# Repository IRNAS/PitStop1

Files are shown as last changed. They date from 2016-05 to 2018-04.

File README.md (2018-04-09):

# PitStop1 - Open source turtle tag and turtle camera enclosure
PitStop1 is open source turtle tag enclosure we developed in collaboration with the [Arribada Initiative](http://blog.arribada.org/). Turtle tags are used to track the movement of turtles and collect the information necessary to design better strategies for their conservation.

In this repository you can find all technical documentation for the latest version of the turtle tag enclosure and the turtle camera enclosure. The documentation for the version 1 of Pitstop1 is available in the branch [version-1](https://github.com/IRNAS/PitStop1/tree/version1).

Read [an article about the open source turtle tags and the development process](https://www.wildlabs.net/resources/case-studies/how-open-source-technologies-could-dramatically-reduce-cost-tagging-green-sea) and get in touch with [us at Institute IRNAS](http://irnas.eu) for customization and orders.

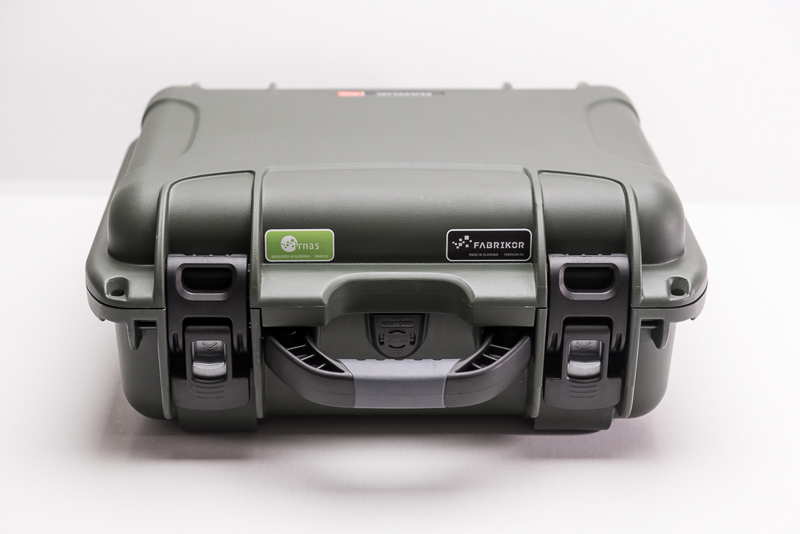
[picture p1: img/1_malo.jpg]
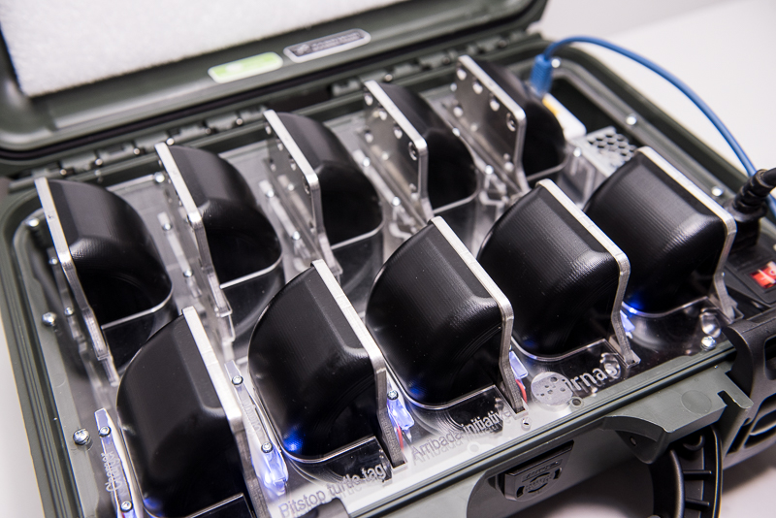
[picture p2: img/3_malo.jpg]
    

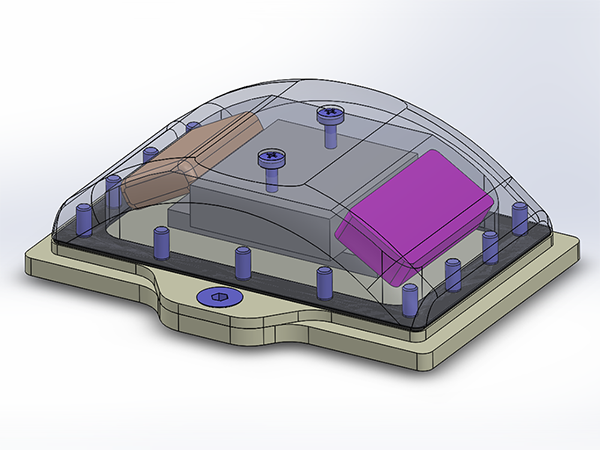
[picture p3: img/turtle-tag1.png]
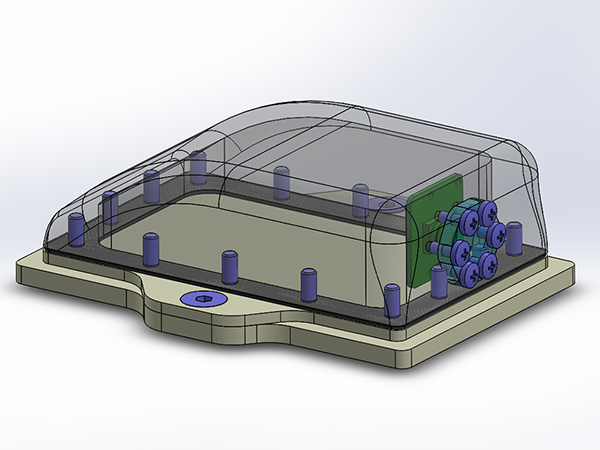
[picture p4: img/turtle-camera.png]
 

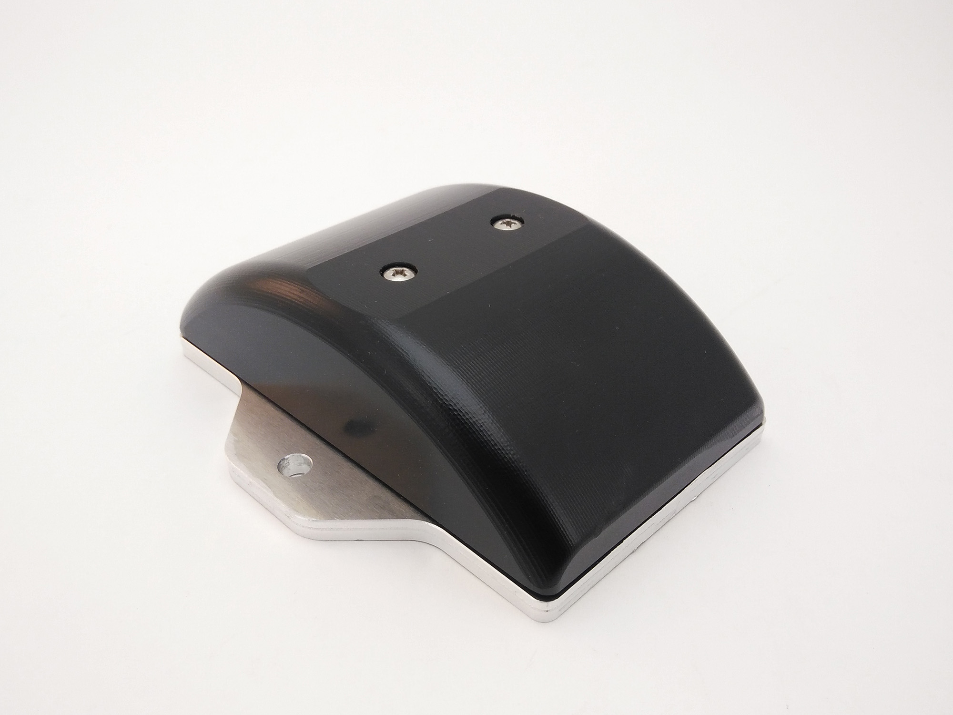
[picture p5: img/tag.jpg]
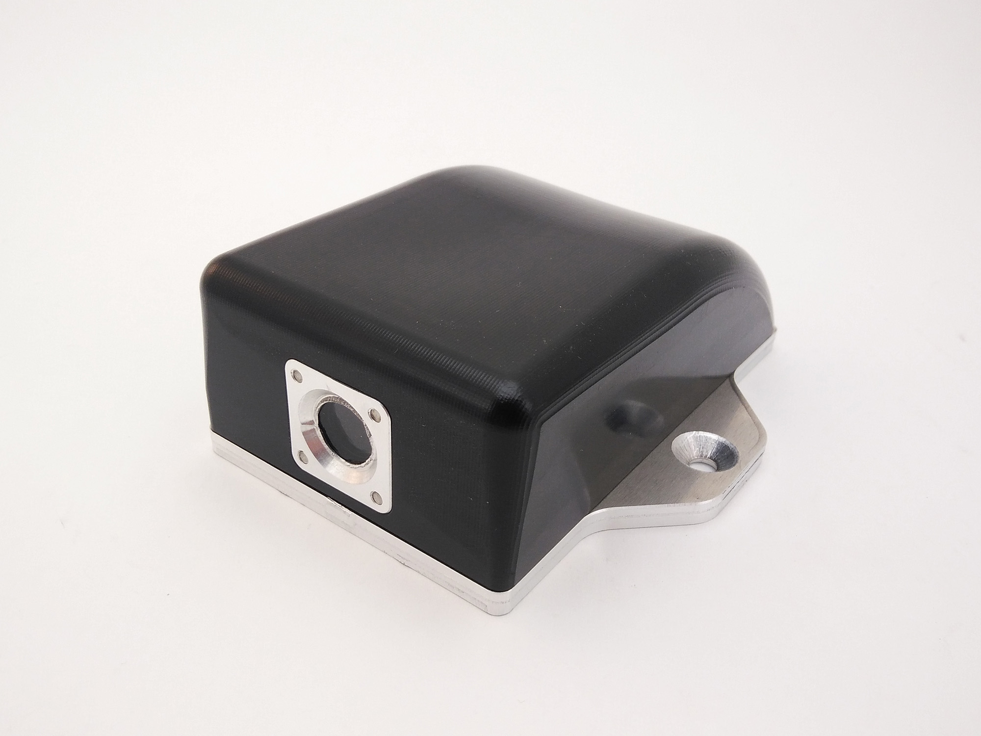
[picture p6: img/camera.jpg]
 

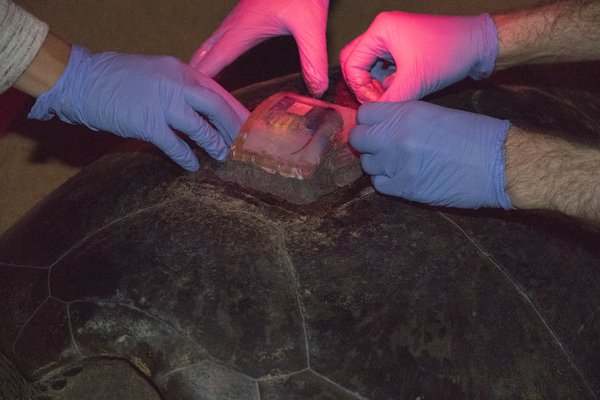
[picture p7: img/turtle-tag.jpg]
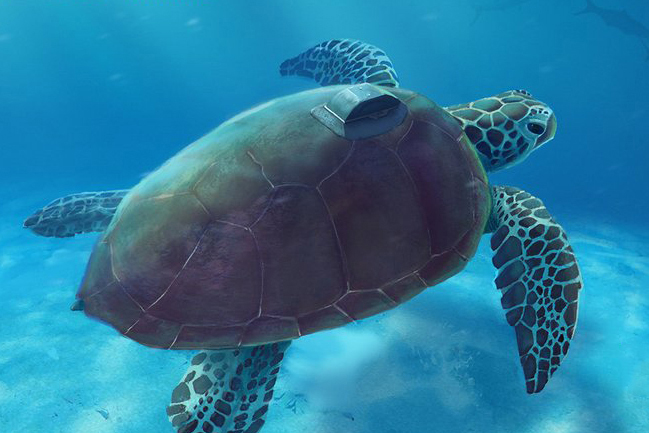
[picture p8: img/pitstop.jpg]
 
*Copyright: The Arribada Initiative*

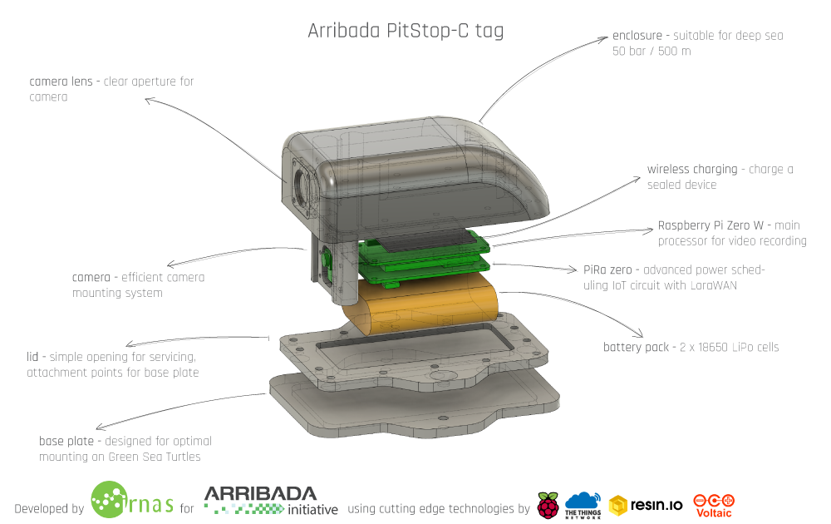
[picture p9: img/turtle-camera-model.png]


#### Testing

The enclosure has to sustain in extreme circumstances while mounted on the turtle, such as being hit by rocks, the turtle rubs its shell at, or high pressure at depths up to 200m. To determine what material and sealing to use for the enclosure we did a series of <a href="https://github.com/IRNAS/PitStop1/tree/master/testing">tests</a>.

---

#### License

All our projects are as usefully open-source as possible.

Hardware including documentation is licensed under [CERN OHL v.1.2. license](http://www.ohwr.org/licenses/cern-ohl/v1.2)

Firmware and software originating from the project is licensed under [GNU GENERAL PUBLIC LICENSE v3](http://www.gnu.org/licenses/gpl-3.0.en.html).

Open data generated by our projects is licensed under [CC0](https://creativecommons.org/publicdomain/zero/1.0/legalcode).

All our websites and additional documentation are licensed under [Creative Commons Attribution-ShareAlike 4 .0 Unported License] (https://creativecommons.org/licenses/by-sa/4.0/legalcode).

What this means is that you can use hardware, firmware, software and documentation without paying a royalty and knowing that you'll be able to use your version forever. You are also free to make changes but if you share these changes then you have to do so on the same conditions that you enjoy.

Koruza, GoodEnoughCNC and IRNAS are all names and marks of Institut IRNAS Rače.
You may use these names and terms only to attribute the appropriate entity as required by the Open Licences referred to above. You may not use them in any other way and in particular you may not use them to imply endorsement or authorization of any hardware that you design, make or sell.

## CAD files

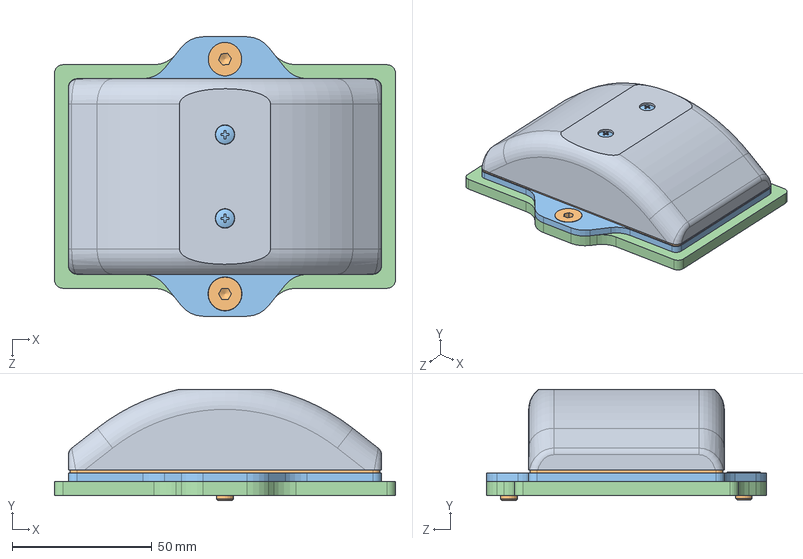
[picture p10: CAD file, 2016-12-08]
source/turtle tag.SLDASM
122.0 x 39.9 x 100.0 mm
case
gasket
lid
base plate
meraki
AX3
i-gotU
battery 1050mAh LiPo
screw_HEX_SOCKET_DIN7991_M4x12_8.8 x 14
screw_HEX_SOCKET_DIN7991_M6x10_8.8 x 2
screw_selfsealing_phillips_335-1156-ND_M3x8 x 2

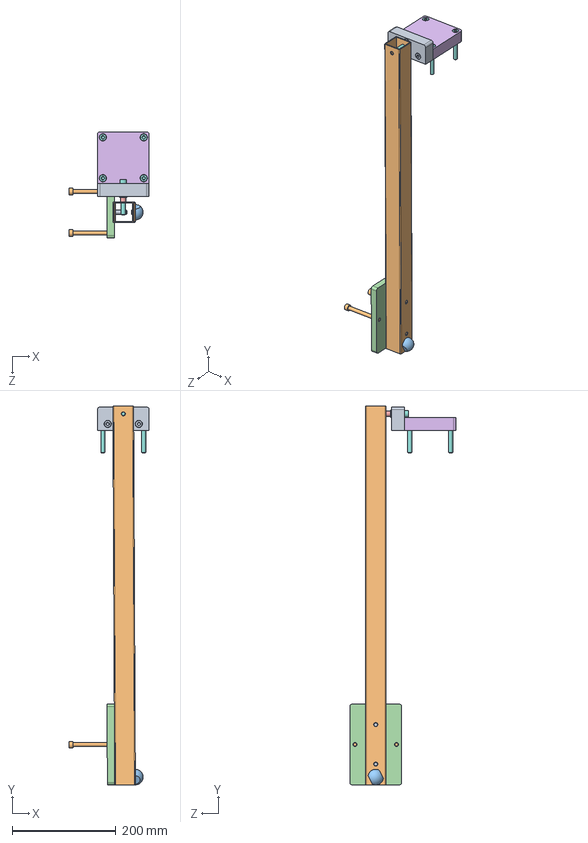
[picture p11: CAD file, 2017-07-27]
testing/durability/pendulum/Assembly.SLDASM
155.0 x 730.2 x 205.0 mm
holder2
lever
backplate
spacer
holder1
DIN 912 M5 x 12
DIN 912 M8 x 60 x 5
DIN 912 M8 x 30 x 4
DIN 912 M8 x 80 x 2

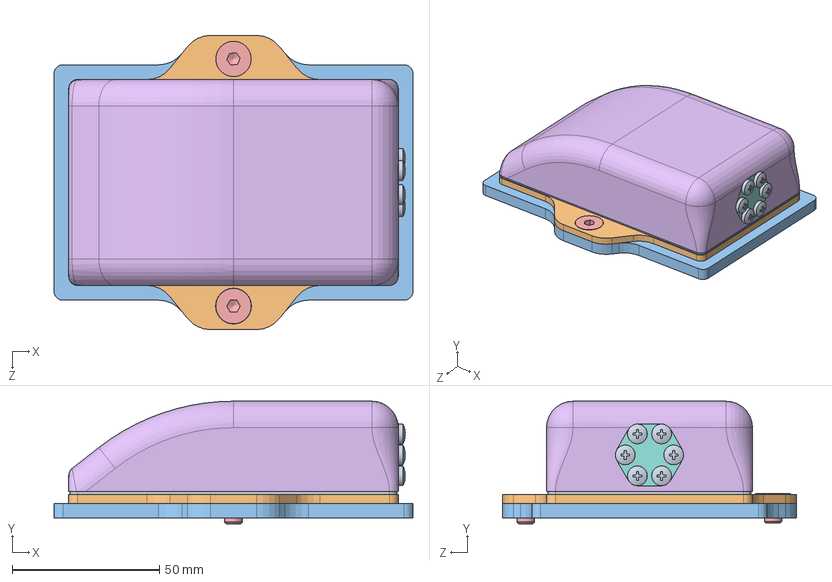
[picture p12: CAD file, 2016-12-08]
source/turtle camera.SLDASM
122.0 x 41.7 x 100.0 mm
gasket
lid
base plate
screw_HEX_SOCKET_DIN7991_M4x12_8.8 x 14
screw_HEX_SOCKET_DIN7991_M6x10_8.8 x 2
case for camera
camera
camera glass
screw_selfsealing_phillips_335-1156-ND_M3x8 x 6

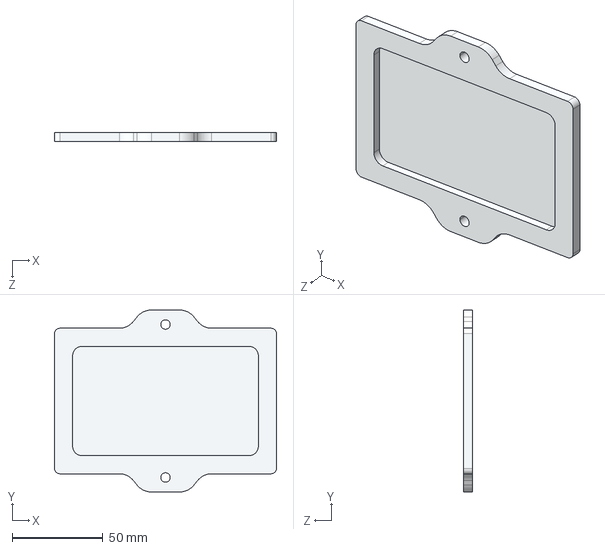
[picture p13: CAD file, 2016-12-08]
documentation turtle tag/base plate.STEP
122.0 x 100.0 x 5.00 mm

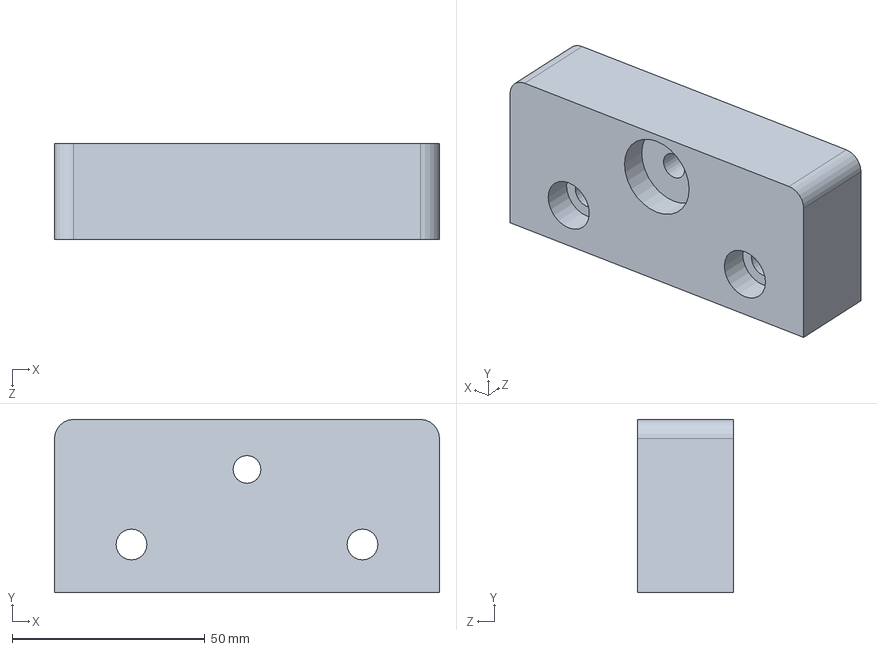
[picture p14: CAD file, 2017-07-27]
testing/durability/pendulum/holder2.SLDPRT
100.0 x 45.0 x 25.0 mm

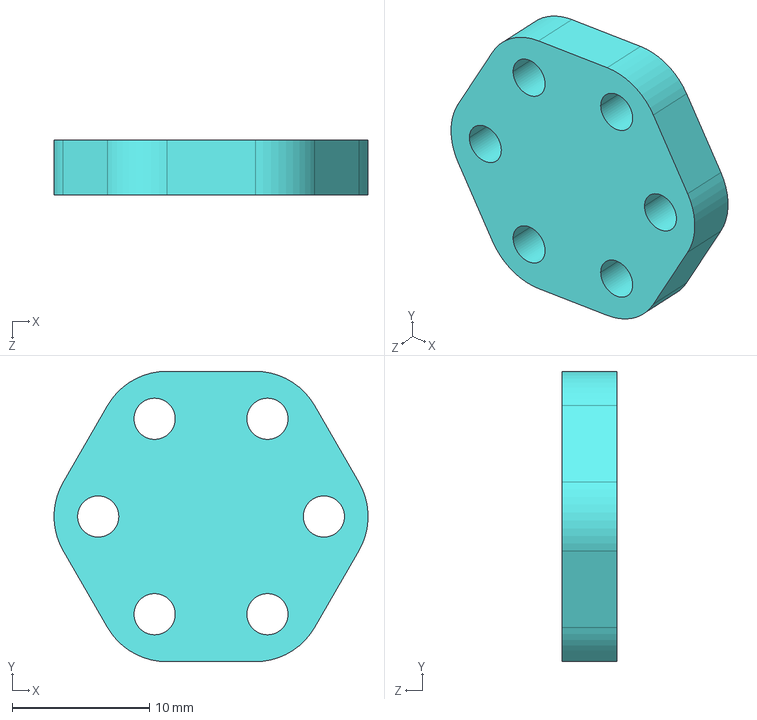
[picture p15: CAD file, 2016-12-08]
documentation turtle camera/camera glass.STEP
22.9 x 21.2 x 4.00 mm

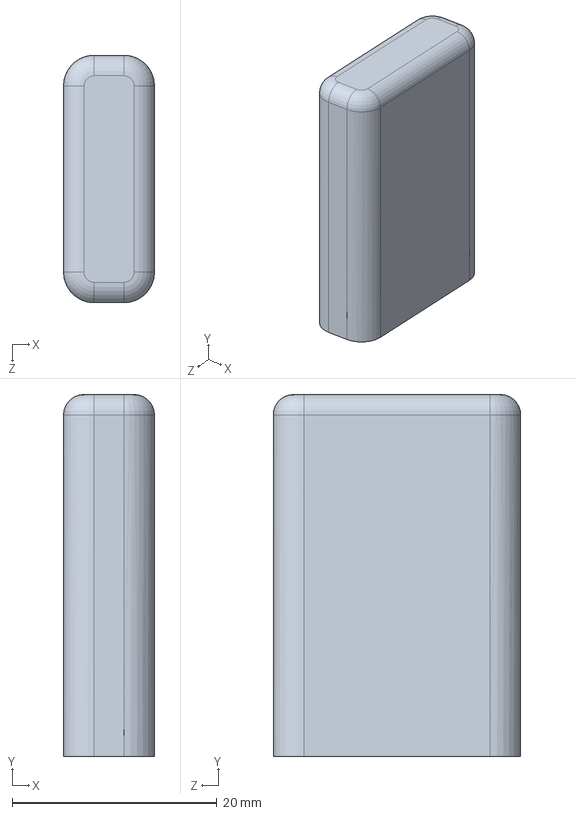
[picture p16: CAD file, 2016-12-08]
source/AX3.SLDPRT
8.90 x 35.4 x 24.2 mm

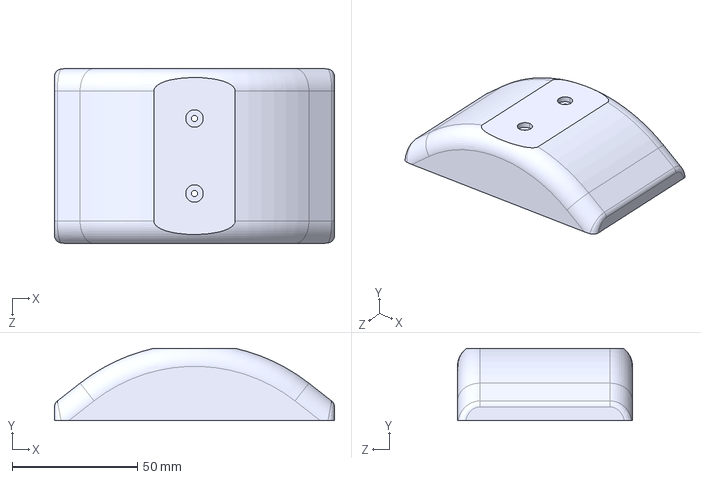
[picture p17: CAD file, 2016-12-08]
documentation turtle tag/case.STEP
112.0 x 29.0 x 70.0 mm

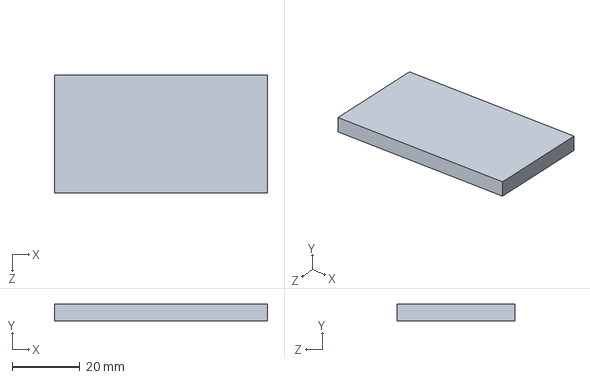
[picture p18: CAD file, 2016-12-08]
source/battery 1050mAh LiPo.SLDPRT
63.0 x 5.00 x 35.0 mm

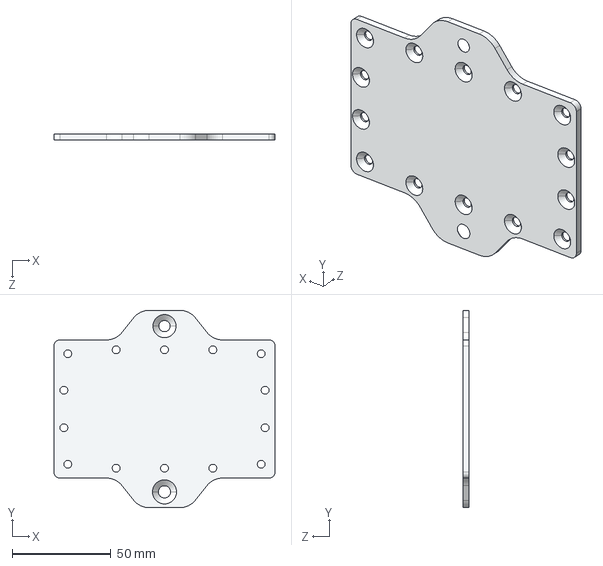
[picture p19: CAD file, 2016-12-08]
documentation turtle camera/lid.STEP
112.0 x 100.0 x 3.00 mm

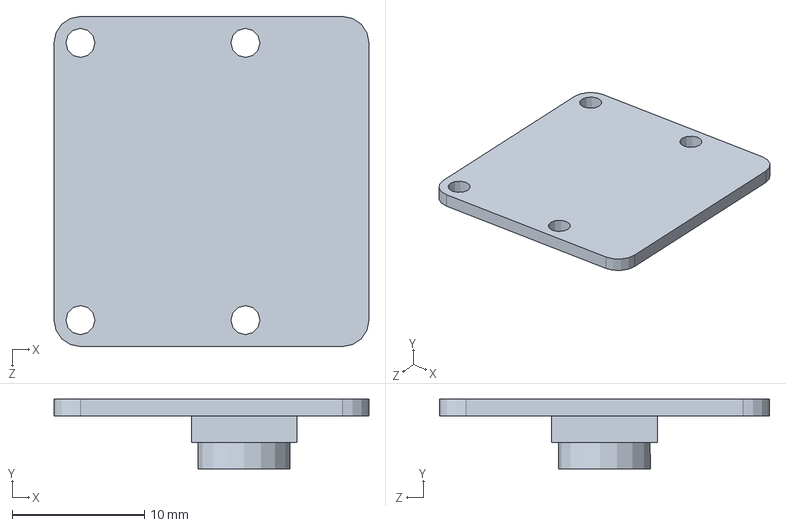
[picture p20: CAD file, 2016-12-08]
source/camera.SLDPRT
23.9 x 5.30 x 25.0 mm

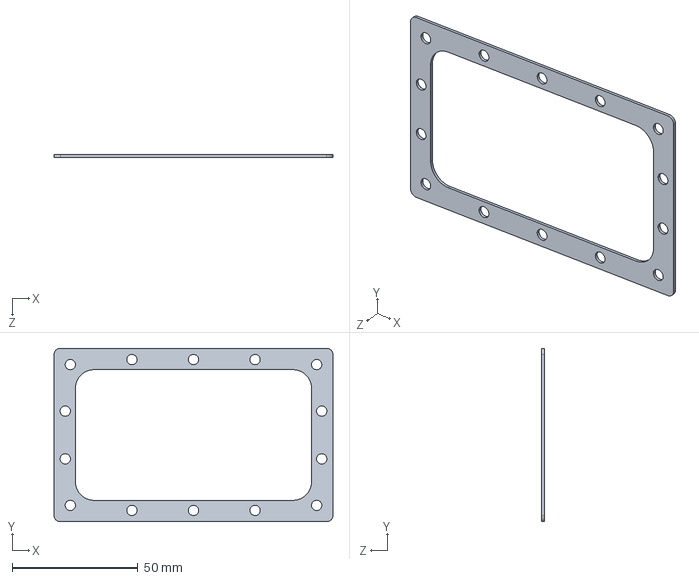
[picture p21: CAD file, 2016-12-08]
documentation turtle camera/gasket.STEP
111.0 x 69.0 x 1.00 mm

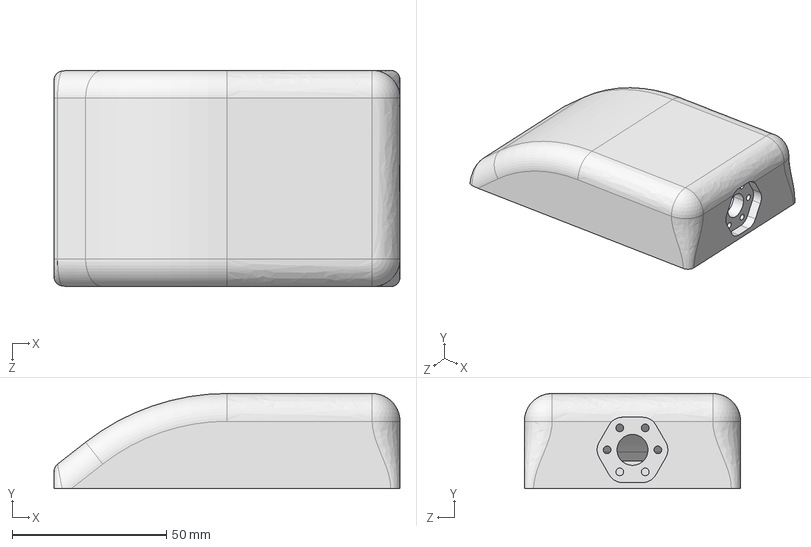
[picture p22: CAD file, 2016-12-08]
documentation turtle camera/case for camera.STEP
112.0 x 30.8 x 70.0 mm

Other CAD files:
documentation turtle camera/turtle camera.STEP
documentation turtle tag/turtle tag.STEP
documentation turtle camera/base plate.DXF
documentation turtle camera/camera glass.DXF
documentation turtle camera/gasket.DXF
documentation turtle camera/lid.DXF
documentation turtle tag/base plate.DXF
documentation turtle tag/gasket.DXF
documentation turtle tag/lid.DXF
source/base plate.SLDPRT
source/camera glass.SLDPRT
source/case for camera.SLDPRT
source/case.SLDPRT
source/gasket.SLDPRT
source/i-gotU.SLDPRT
source/lid.SLDPRT
source/meraki.SLDPRT
source/screw_HEX_SOCKET_DIN7991_M4x12_8.8.SLDPRT
source/screw_HEX_SOCKET_DIN7991_M6x10_8.8.SLDPRT
source/screw_selfsealing_phillips_335-1156-ND_M3x8.SLDPRT
source/turtle camera.SLDDRW
source/turtle tag.SLDDRW
testing/durability/pendulum/DIN 912 M5 x 12.SLDPRT
testing/durability/pendulum/DIN 912 M8 x 30.SLDPRT
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

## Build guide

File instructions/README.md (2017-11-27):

# Assembly instructions for PitStop Turtle Camera

Take assembled Raspberry Pi Zero W stack with PiRA Zero, wirelles charging and Raspberry Pi Camera Module.

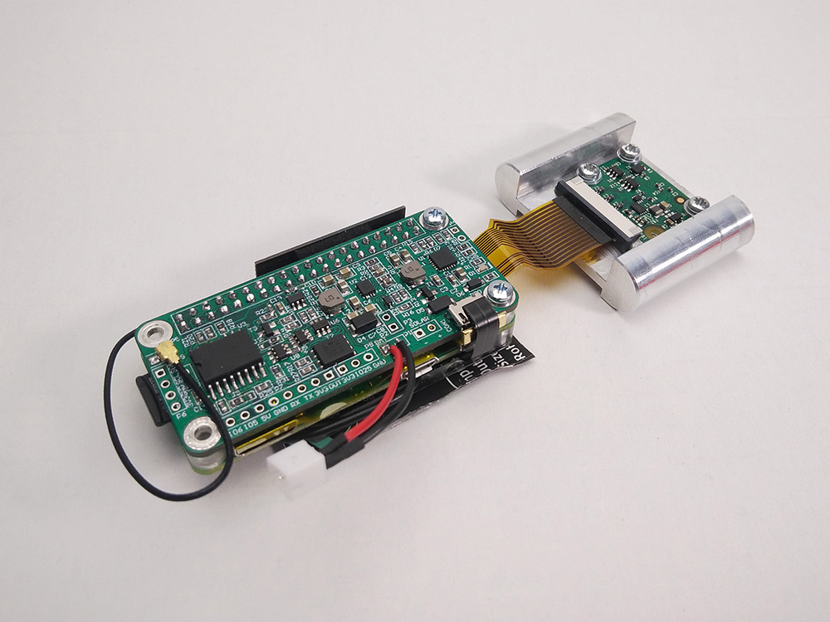
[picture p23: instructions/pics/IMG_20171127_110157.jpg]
<span>
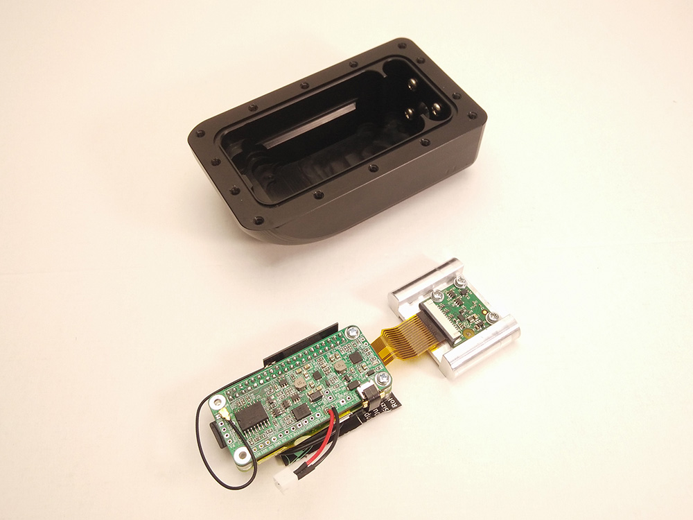
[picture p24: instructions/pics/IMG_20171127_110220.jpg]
</span>

Slide camera in the designed slot and attach the Raspberry Pi Zero stack using two M2.5 screws.

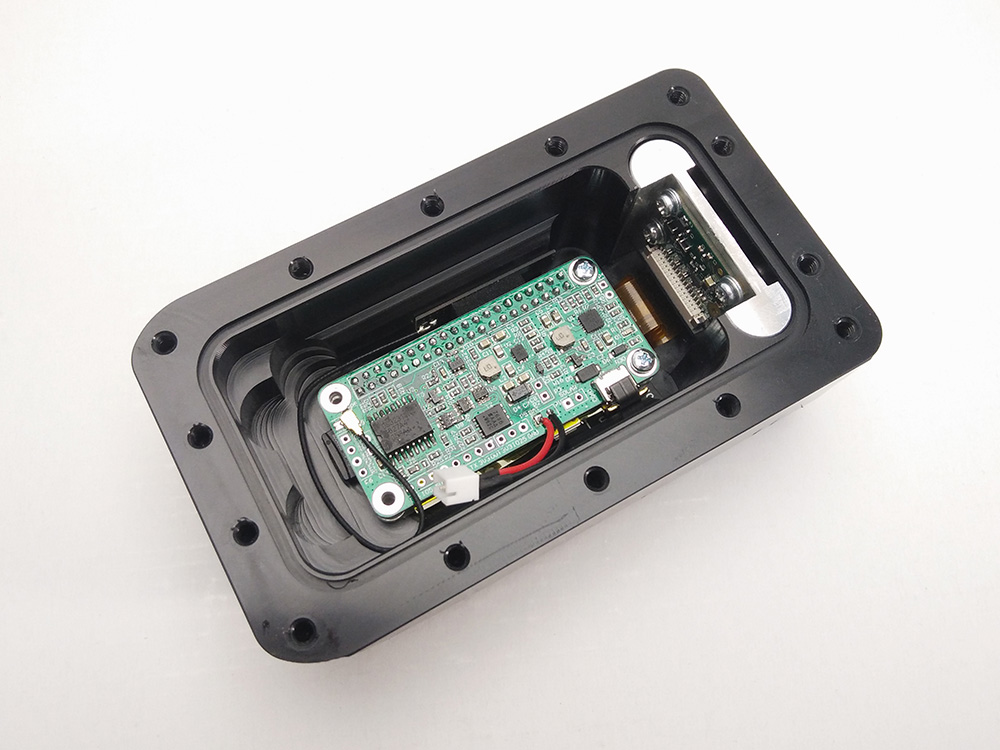
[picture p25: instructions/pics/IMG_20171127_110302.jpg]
<span>
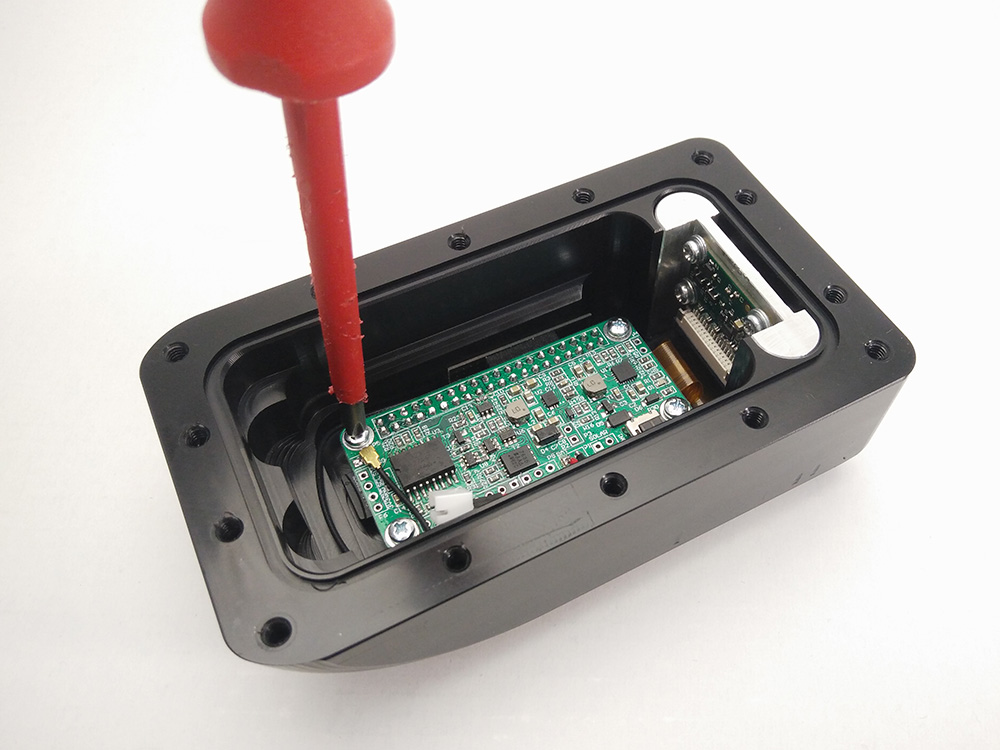
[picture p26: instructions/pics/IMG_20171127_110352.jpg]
</span>

Connect the battery and put it inside the case.

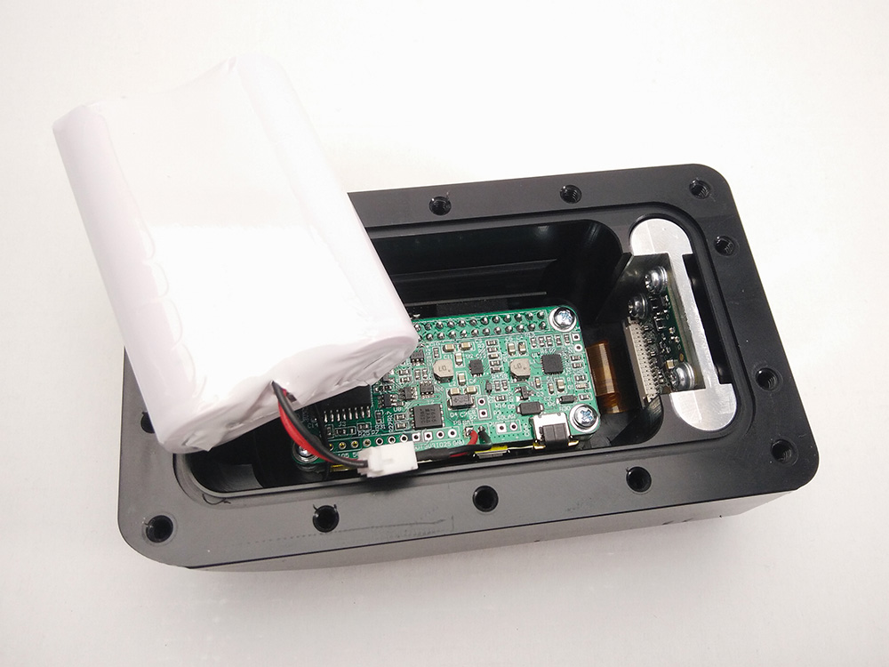
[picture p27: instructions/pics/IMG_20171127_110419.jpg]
<span>
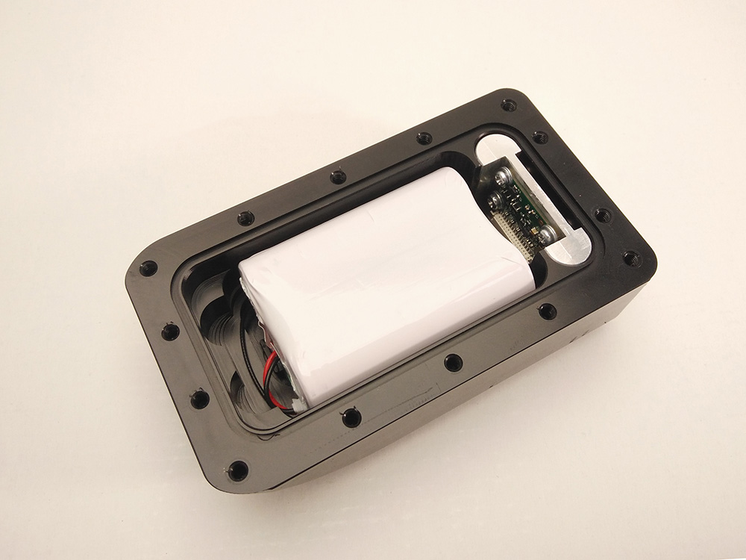
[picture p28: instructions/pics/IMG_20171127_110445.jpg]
</span>

Insert the O-ring in the slot.

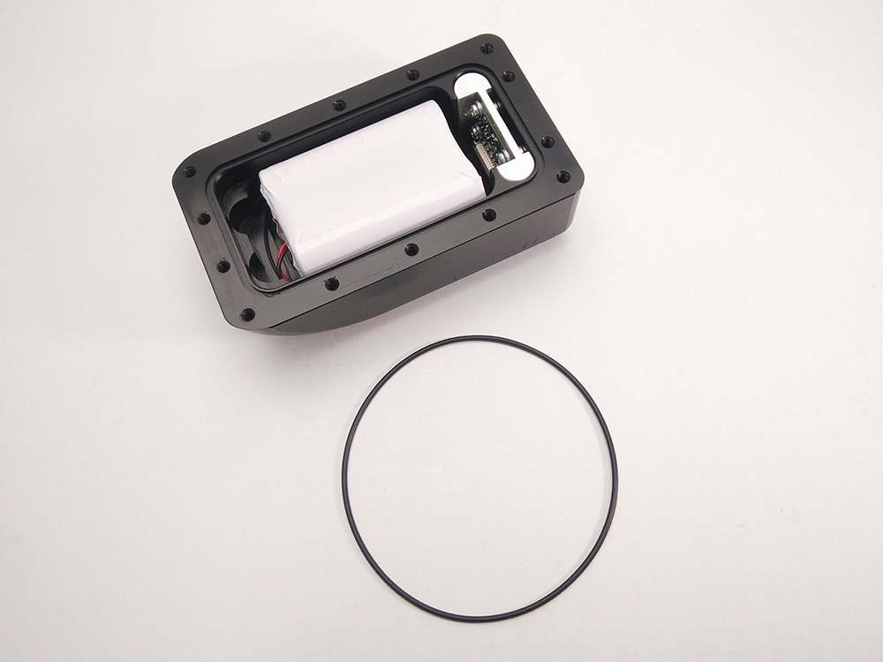
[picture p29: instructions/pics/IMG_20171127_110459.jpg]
<span>
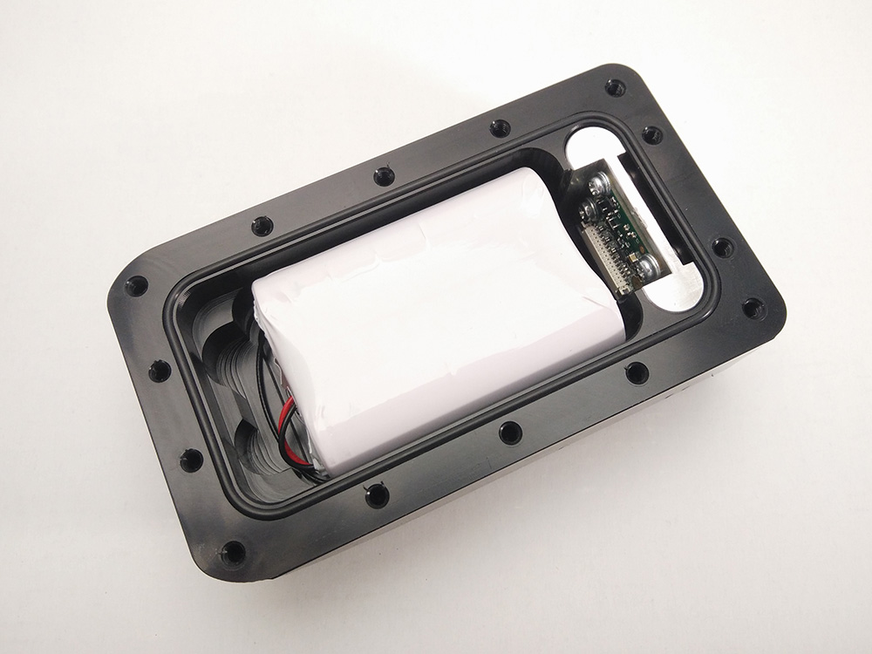
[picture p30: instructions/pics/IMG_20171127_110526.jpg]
</span>

Attch the lid using fourteen M4 screws.

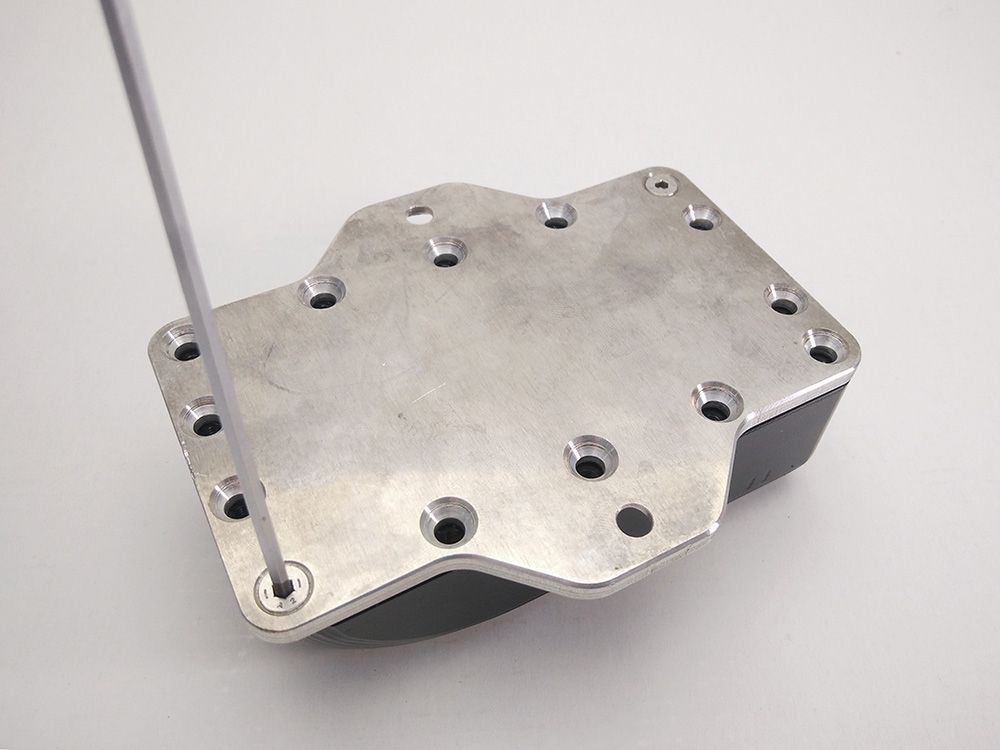
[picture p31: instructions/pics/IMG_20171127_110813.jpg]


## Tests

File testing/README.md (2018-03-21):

# Testing enclosures

The sea turtle regularly cleans its shell by rubbing it at rocks. To sustain the high forces that can occur, the material the enclosure is made of must have high durability. Since the turtle spends most of the time underwater and dives up to 200m deep, the enclosures also have to survive and keep water away under very high pressure. To determine what material and what sealing to use for the enclosure to protect its inside components under those circumstances, we've done a series of tests:  

1) <a href="https://github.com/IRNAS/PitStop1/tree/master/testing/sealing">_**Sealing Test**_</a>
  * testing enclosures made of different materials with different sealings in a pressure container to see if water leaks in under high pressure

<br />

2) <a href="https://github.com/IRNAS/PitStop1/tree/master/testing/durability">_**Durability Test**_</a>
  * testing enclosures made of different materials with a pendulum like construction to see which material survives best on impact with high momentum

<br />

3) <a href="https://github.com/IRNAS/PitStop1/tree/master/testing/high%20pressure%20sealing">_**High Pressure Sealing Test**_</a>
  * testing PitStop Tag and Camera enclosures under high pressure up to 25 bar, equal to the depth of 250m

<br />

4) <a href="https://github.com/IRNAS/PitStop1/tree/master/testing/high%20pressure%20durability">_**High Pressure Durability Test**_</a>
  * testing PitStop Camera enclosures under high pressure and observing deformations on the enclosures

<br />

5) <a href="https://github.com/IRNAS/PitStop1/tree/master/testing/pressure%20sensor">_**Pressure Sesnsor Sealing Test**_</a>
  * testing the sealing of the pressure sensor for PitStop Tags

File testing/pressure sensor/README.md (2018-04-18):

# Pressure sensor sealing test report

## Goal
For accurate tracking of the sea turtles the information about the depth is very important. A pressure sensor will be used in the PitStop Tags to measure the depth. Sealing tests of the pressure sensor were similar to the sealing tests of the PitStop Tag enclosures. A special enclosure was made from polyoxymethylene (POM) plastics with rubber O-ring string and an O-ring gasket used for sealing. Enclosure with the pressure sensor was put under high pressure up to 10 bar, equal to the depth of 100m.

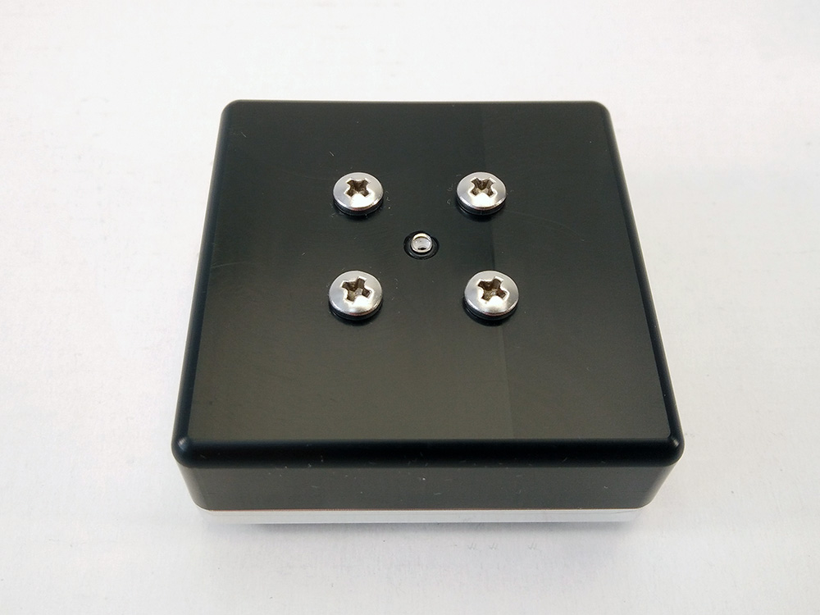
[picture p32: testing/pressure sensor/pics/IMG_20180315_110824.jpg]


## Equipment
* Pressure container

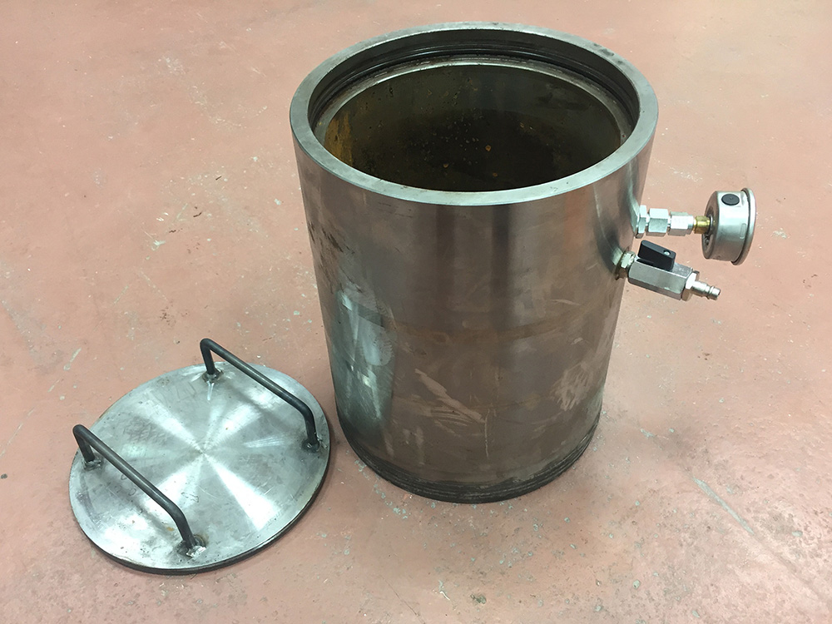
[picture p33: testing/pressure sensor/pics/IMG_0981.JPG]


* Circlip and pliers

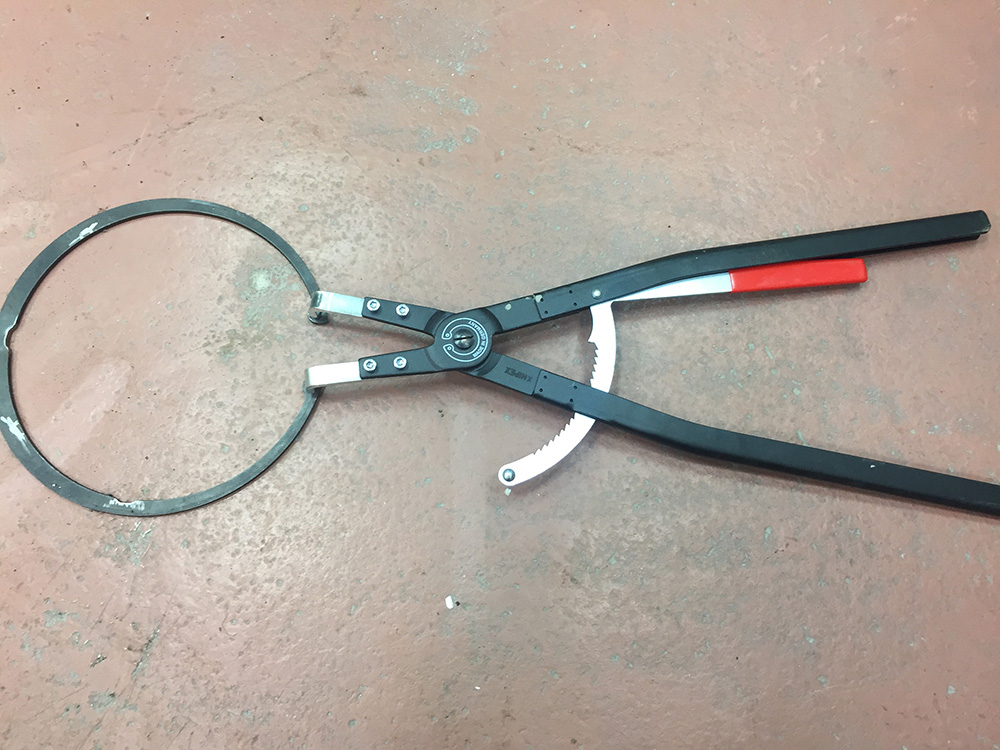
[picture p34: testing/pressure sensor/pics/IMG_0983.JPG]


* Air hose under pressure

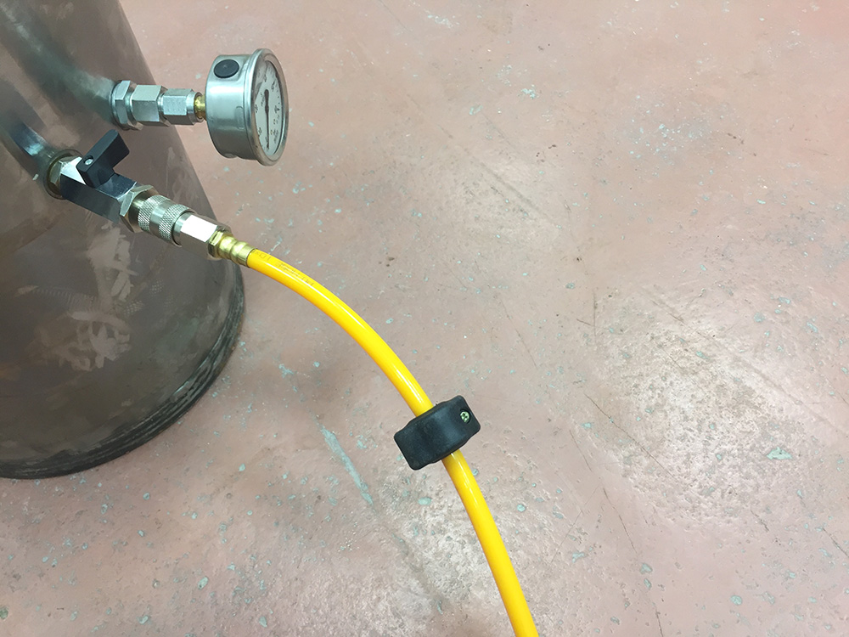
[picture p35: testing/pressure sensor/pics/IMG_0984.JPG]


## Tested enclosure and pressure sensor
* Special enclosure for the pressure sensor

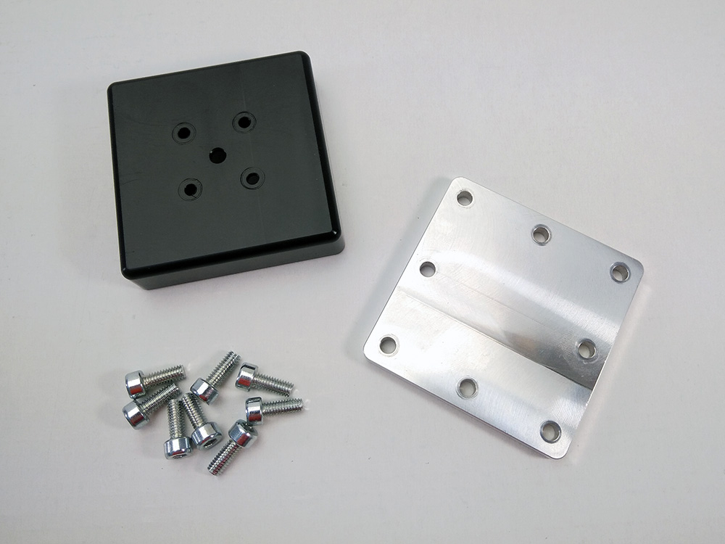
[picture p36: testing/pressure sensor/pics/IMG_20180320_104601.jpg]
<span>
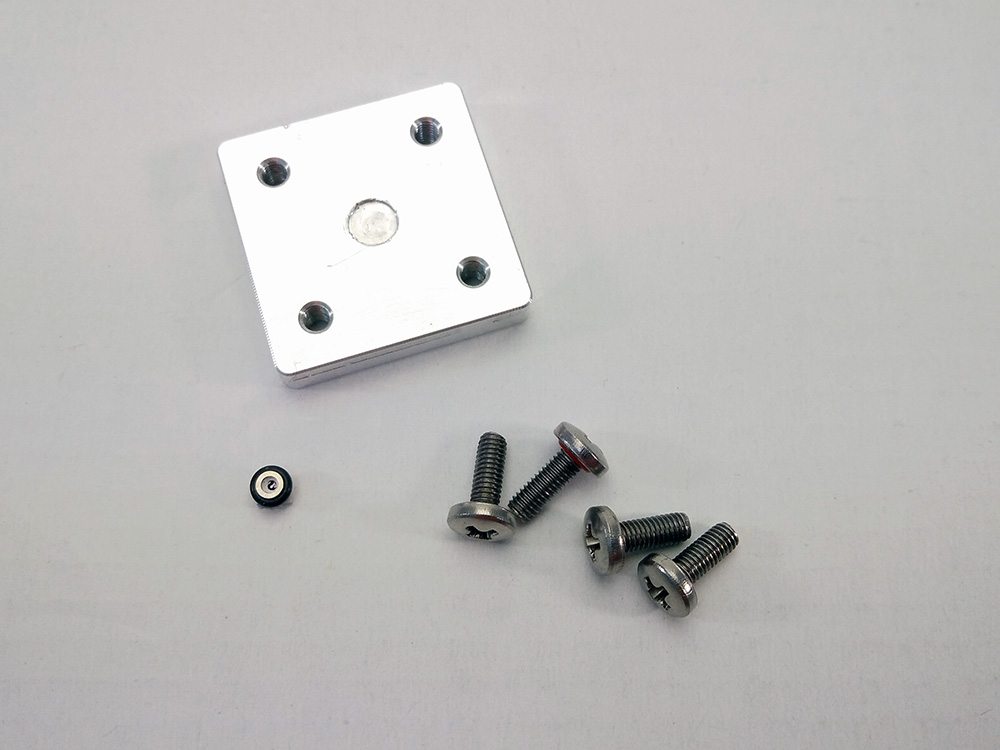
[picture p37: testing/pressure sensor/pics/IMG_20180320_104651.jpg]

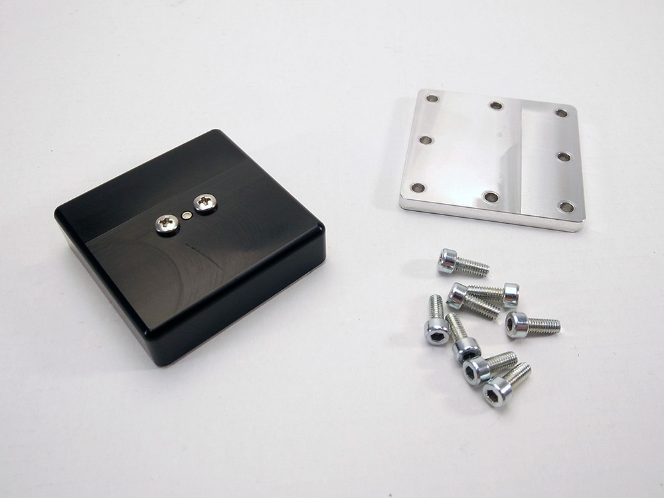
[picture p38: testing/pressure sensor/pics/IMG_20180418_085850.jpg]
</span>

* TE Connectivity MS5837-30BA Pressure Sensor (http://www.te.com/usa-en/product-CAT-BLPS0017.html) with O-ring gasket

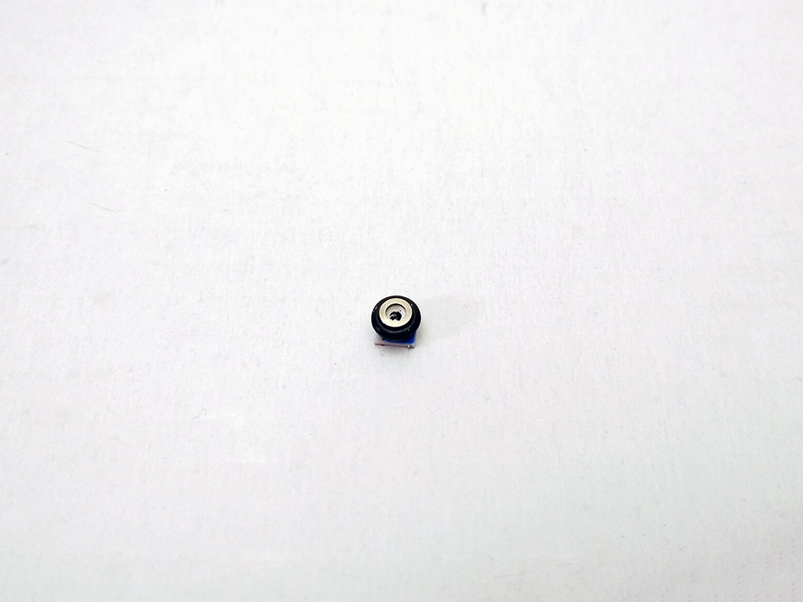
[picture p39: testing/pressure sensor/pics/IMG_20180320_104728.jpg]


* A custom PCB, designed to attach and connect the pressure sensor

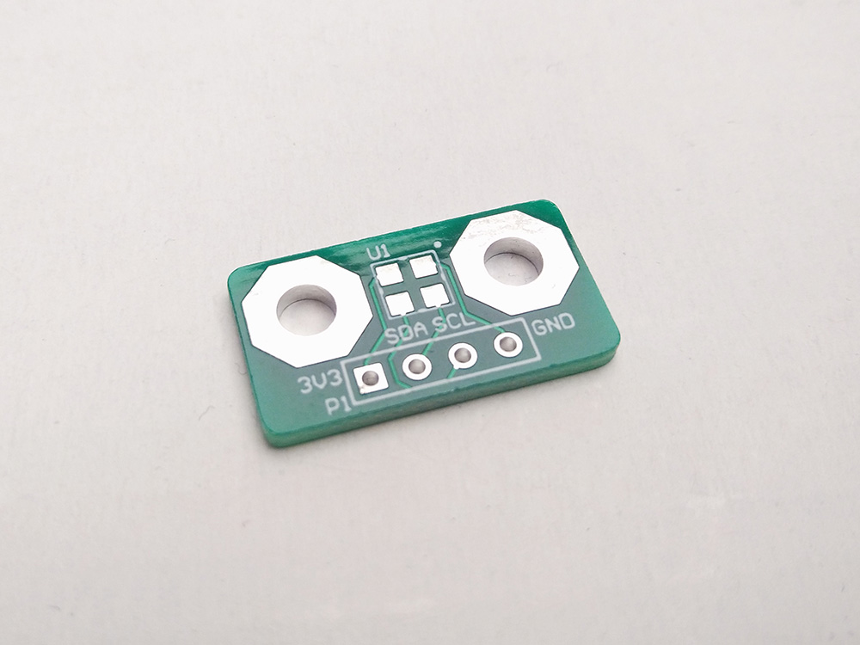
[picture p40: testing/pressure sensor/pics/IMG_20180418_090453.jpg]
<span>
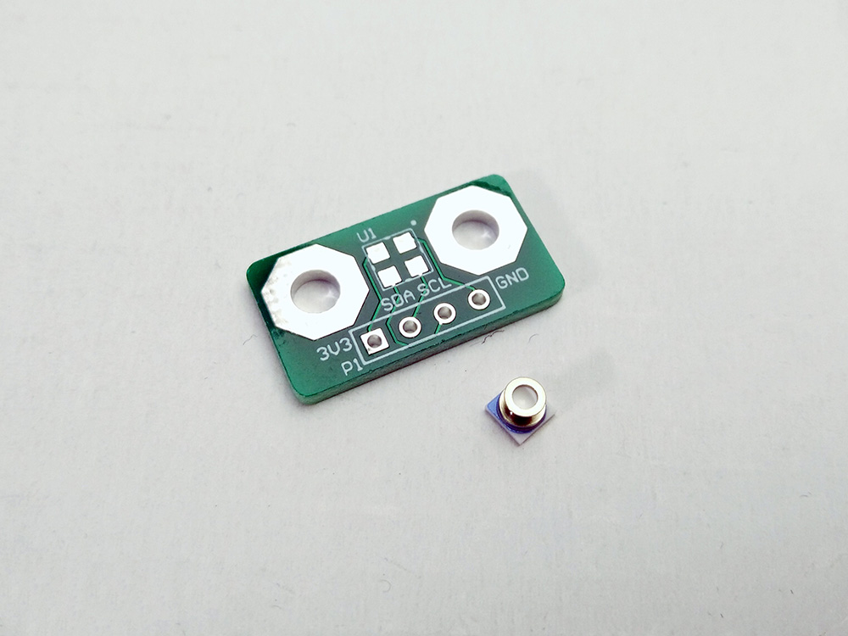
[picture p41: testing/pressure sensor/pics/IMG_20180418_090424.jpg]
</span>

## Testing
To test how the pressure sensor can handle the pressure in water we used a pressure container.

The container was filled half way up with water. The tested enclosure was assembled and put on the bottom of the container fully covered with water. The container was sealed with the cover and a circlip and the air hose was attached. The enclosure with the pressure sensor was tested under 10 bars of pressure for 60 min. Afterwards it was taken out and the backplate was unscrewed from the rest of the case very carefully so no water from the outside of the case would flow inside accidently.

In the first two tests we used an aluminium plate to attach the pressure sensor. We have then designed a custom PCB which will be used to attach and connect the pressure sensor in the actual PitStop Tags. In the third test we then used the PCB to attach the pressure sensor.

## Results
During the assembly the pressure sensor was damaged when inserted into the special enclosure due to the incorrect O-ring size. Because of the damage the water was able to penetrate the pressure sensor and fully flooded the case. The sealing test was unsuccessful and therefore had to be repeated with the correct O-ring size and a new pressure sensor.

<span>
</span>

Another test with a new pressure sensor and the correct O-ring was conducted. This time the case stayed completely dry.

<span>
</span>

In the third test we used a custom PCB which is used to attach and connect the pressure sensor. The case stayed completely dry.

<span>
</span>

## Conclusion
The first test of the pressure sensor was unsuccessful because the sensor was damaged during the assembly. Because of the damage the water was able to penetrate the pressure sensor. The sealing test was then repeated with the correct O-ring size and a new pressure sensor. In the second test the case stayed completely dry. In the third test we used a custom PCB which will be used to attach and connect the pressure sensor in the actual PitStop Tags. We confirmed the sealing with the PCB as well.

The prescribed sealing method for the pressure sensor was confirmed, but more tests at 25 bar of pressure should be conducted to confirm the sealing under high pressure equal to the depth of 250m.

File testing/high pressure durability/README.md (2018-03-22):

# High pressure durability test report

## Goal
During the high pressure sealing test where we were testing the sealing of the enclosures under high pressure we have noticed a large deformation when the enclosure was exposed to 50 bar of pressure and decided that it had to be further investigated. We have used PitStop Camera enclosures made from polyoxymethylene (POM) and polyethylene (PE) plastics for these tests. POM was selected as the most appropriate in the first durability and sealing tests and the PE was selected as it has a lot lower density. Cases made from PE would therefore weigh a lot less and might have less impact on sea turtles' behaviour. Enclosures were put under high pressure up to 25 bar, equal to the depth of 250m.



## Equipment
* Pressure container



* Circlip and pliers



* Air hose under pressure



* High pressure air tank and regulator



## Tested enclosures
* PitStop Camera enclosure, made from polyoxymethylene (POM) plastics - weight: 208 g



* PitStop Camera enclosure, made from polyethylene (PE) plastics - weight: 144 g



## Testing
We again used a pressure container to test the sealing of the enclosures. Tests were similar to the sealing tests. The tested cases were assembled and put on the bottom of the container fully covered with water. The container was sealed with a cover and a circlip and the air hose from the high pressure air tank was connected.

The POM cases were tested under 10 and 25 bar of pressure for 30 minutes while the PE cases were tested under 5 and 8 bar of pressure for 30 minutes, 1 and 16 hours. After each test cases were taken out of the container and wiped. The deformation was measured using a depth gage.

## Results
* Polyoxymethylene (POM) plastics - 10 bar of pressure for 30 minutes

There was no noticeable deformation.



* Polyoxymethylene (POM) plastics - 25 bar of pressure for 30 minutes

There was no noticeable deformation.



* Polyethylene (PE) plastics - 5 bar of pressure for 30 minutes

We have measured a maximum 1.1 mm deformation at the top middle of the case.



* Polyethylene (PE) plastics - 8 bar of pressure for 30 minutes

We have measured a maximum 1.1 mm deformation at the top middle of the case.



* Polyethylene (PE) plastics - 8 bar of pressure for 1 hour

We have measured a maximum 1.6 mm deformation at the top middle of the case.



* Polyethylene (PE) plastics - 8 bar of pressure for 16 hours

We have measured a maximum 5.4 mm deformation at the top middle of the case. Unfortunately, no image of this test is available.

## Conclusion
While enclosure made from polyoxymethylene (POM) passed both tests, we have discovered that the enclosure made from polyethylene (PE) was a lot weaker. Tests under only 8 bar showed a large deformation and we have therefore concluded that PE is not suitable for PitStop Tag and Camera enclosures if the design remains unchanged. If the wall thickness of the enclosure would be increased PE could be suitable as well but more tests should be conducted to confirm that.

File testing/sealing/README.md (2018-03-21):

# Sealing test report

## Goal
The turtles can swim very deep where the pressure is high, that is why the cases have to resist water under high pressure to protect the electronics inside. We put our cases into a pressure container to see which material and which sealing resists water best.

## Equipment
* Pressure container



* Circlip and pliers



* Air hose under pressure



## Tested materials
* Polyoxymethylene (POM) - foamed polyurethan O-ring string



* Polyoxymethylene (POM) - rubber O-ring string



* Polyoxymethylene (POM) - polyurethan sealing sheet



* Oleamide - polyurethan sealing sheet



* Polyamide 6 (PA6) - polyurethan sealing sheet



* Acryl - hard polyurethan sealing layer



## Testing
To test how the cases can handle pressure in water we used a pressure container.

The container was filled half way up with water. The tested cases were assembled and put on the bottom of the container fully covered with water. Weights had to be attached so the cases stayed static on the bottom of the container during the test. The container was sealed with the cover and a circlip and the air hose was attached. The cases were tested under 9 bars of pressure for 15 min. Afterwards they were taken out and the backplate was unscrewed from the rest of the case very carefully so no water from the outside of the case would flow inside accidently.

## Results
* Polyoxymethylene (POM) - foamed polyurethan O-ring string

The case was wet on the backplate and on the inside. There was water already flowing out while unscrewing the backplate so it can be assumed there was a lot of water inside.

<span>

</span>

* Polyoxymethylene (POM) - rubber O-ring string

The only case without any wet spots on the inside. This case didn't have screws on the top which could be a reason why it stayed dry. Also the thread on one of the backplate screws got broken but it didn't effect the water resistance of the case.

<span>

</span>

* Polyoxymethylene (POM) - polyurethan sealing sheet

There was a very small wet spot at one of the top screws but it has already disappeared at the time of taking the picture so it's not visible.

<span>

</span>

* Oleamide - polyurethan sealing sheet

Of all the cases with a polyurethan sealing sheet this one was the wettest. There were big wet spots on the inside of the case.

<span>

</span>

* Polyamide 6 (PA6) - polyurethan sealing sheet

It only had a tiny spot at one of the screws which is visible on the picture.

<span>

</span>

* Acryl - hard polyurethan sealing layer

It was already visible from the outside that a lot of water penetrated the case during the testing.

<span>

</span>

* Polyoxymethylene (POM) - O-ring string

Second try with the same POM case with the O-ring sealing we used before, only this time it had screws on the top. It was still completely dry even with the screws.

<span>

</span>

## Conclusion
* The acrylic with hard polyurethan sealing layer and the POM with polyurethan O-ring sealing string cases leaked a lot of water.
* The ones with the polyurethan sealing sheet between leaked a little. It might have also leaked at the screws on top because it was wet mainly near the screws.
* The case with the O-ring sealing string held up best without any leaking.

At first we suspected that the screws on top could have something to do with the leaking because the wet spots were often near the screws. Since the only completely dry case was the POM with the O-ring sealing which didn't have holes on top, we made new holes into the case to determine if the screws are the reason of leaking. The results show that the case stayed dry even after we drilled the holes which means that the sealings were the leaking reason of all the tests where it leaked.

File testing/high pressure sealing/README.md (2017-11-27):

# High pressure sealing test report

## Goal
After the right material and sealing method were selected, the sealing under high pressure had to be tested as well. For testing we have made a new series of two enclosures, one PitStop Tag enclosure and one PitStop Camera enclosure. We have used polyoxymethylene (POM) for enclosures and rubber O-ring string for sealing. Enclosures were put under high pressure up to 25 bar, equal to the depth of 250m.



## Equipment
* Pressure container



* Circlip and pliers



* High pressure air tank and regulator



## Tested enclosures
* PitStop Tag enclosure

<span>
</span>

* PitStop Camera enclosure

<span>
</span>

## Testing
We again used a pressure container to test the sealing of the enclosures. Tests were similar to the first sealing tests. The tested cases were assembled and put on the bottom of the container fully covered with water. The container was sealed with a cover and a circlip and the air hose from the high pressure air tank was connected.

The cases were first tested under 10 and 25 bars of pressure for 15 minutes. The next test was conducted at 50 bars. The last test was conducted at 25 bars for a few hours to test longer exposure to high pressure. After each test cases were taken out of the container and wiped. The lid was removed from the rest of the case to check for any leaks.

## Results
Both cases, Tag and Camera enclosures, stayed completely dry at 10 and 25 bar. 

<span>
</span>

When tested at 50 bar, slight deformation was found on both aluminium lids and on Camera enclosure. But despite the deformation, both cases stayed completely dry, even at 50 bar.

<span>

</span>

The last test that we conducted was at 25 bars for a few hours. Even at longer exposure to high pressure, both cases stayed completely dry.

## Conclusion
Both cases, PitStop Tag enclosure and PitStop Camera enclosure passed all tests. Even at 50 bar, when both cases have undergone permanent deformation, they stayed completely dry. This confirms our choice of rubber O-ring string for sealing.

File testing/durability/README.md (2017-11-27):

# Durability test report

## Goal

The turtles clean their shells by rubbing them at rocks. Because the turtle is very heavy it would create a lot of force if it hits the spot where the case is mounted. We wanted to know if the tested cases can survive a hit with such high force. Our goal was to see which material absorbs most force at the given shape and to try and simulate a scenario of use of the case.

## Equipment

We have built a pendulum like construction. There is a 73cm long lever with its axis of rotation on a screw that is mounted on a two part holder mounted on the table. The screw is held by two bearings to help make the rotation smoother. There is a nut on the screw between the lever and the holder to keep some distance. At the other end of the lever there's a backplate mounted on the lever with two screws, with two long screws heading out in the opposite direction where the weights can be put on. On the opposite side of the lever there's a small sphere, which hits the target case. On the ground there is a holder that holds the tested case in place. It's mounted on a heavy wooden block. There is a board that shows angles (10°, 20°, 30°, 50°, 60°, 67°) mounted on the table.





## Tested materials
*	Acryl (transparent) - weight: 88g
* Polyoxymethylene (POM) (black) - weight: 102g
* Oleamide (green) - weight: 83g
* Polyamide 6 (PA6) (white) - weight: 83g

## Testing

To see witch material absorbs the most force we let the pendolum crash into the case with different weights from different angles.

We pulled the pendulum up to a certain angle and let it crash into the tested case. After the first crash we stopped it to prevent it from crashing again. We tried to keep the number of hits as low as possible so the case wouldn't break because of the number of hits rather than the force of the hit. We started on low angles and worked our way up. We started our testing without any weights on to get an approximation of what the cases can handle. The Acrylic case broke very fast without any weights on. After that we started putting more and more weights on the backplate of the pendulum and the cases held up more than we expected. The POM case finally broke with already very heavy weights on and the oleamide and PA6 cases wouldn't even break with all the weights that we could fit on the backplate.



#### Weights:
* weight 1 (W1): 1140g
* weight 2 (W2): 825g
* weight 3 (W3): 2075g
* weight 4 (W4): 4985g
* weight 5 (W5): 3610g
* weight 6 (W6): 10085g

#### Equipment weight:
* lever: 1715g
* backplate: 710g

## Results
#### Acryl
* no add. weights

|Angle(°)|<span style="font-weight:normal;color:gray">20</span>  |<span style="font-weight:normal;color:gray">30</span>  |<span style="font-weight:normal;color:gray">40</span>    |
|:-:|:-:|:-:|:-:|
|**Status**   | ok  | ok  |broken|

#### Polyoxymethylene (POM)
* no add. weights

|Angle(°)|<span style="font-weight:normal;color:gray">67</span>  |
|:-:|:-:|
|**Status**   | ok  |

* with W1 (1140g)

|Angle(°)|<span style="font-weight:normal;color:gray">30</span>  |<span style="font-weight:normal;color:gray">40</span>  |<span style="font-weight:normal;color:gray">50</span> |<span style="font-weight:normal;color:gray">67</span>    |
|:-:|:-:|:-:|:-:|:-:|
|**Status**   | ok  | ok  | ok  | ok  |

* -with W1 + W2 (1965g)

|Angle(°)|<span style="font-weight:normal;color:gray">50</span>  |<span style="font-weight:normal;color:gray">67</span>
|:-:|:-:|:-:|
|**Status**   | ok  | ok  |

* with W2+W3 (2900g)

|Angle(°)|<span style="font-weight:normal;color:gray">50</span>  |<span style="font-weight:normal;color:gray">67</span>
|:-:|:-:|:-:|
|**Status**   | ok  | ok  |

* with W1+W2+W3 (4040g)

|Angle(°)|<span style="font-weight:normal;color:gray">67</span>  |
|:-:|:-:|
|**Status**   | ok  |

* with W1+W2+W3+W4 (9025g)

|Angle(°)|<span style="font-weight:normal;color:gray">50</span>  |<span style="font-weight:normal;color:gray">67</span>  |<span style="font-weight:normal;color:gray">67</span>  |
|:-:|:-:|:-:|:-:|
|**Status**   | ok  | ok  |broken|



#### Oleamide

* with W1+W2+W3+W5 (7650g)

|Angle(°)|<span style="font-weight:normal;color:gray">67</span>  |
|:-:|:-:|
|**Status**   | ok  |

* with W1+W2+W3+W4 (9025g)

|Angle(°)|<span style="font-weight:normal;color:gray">67</span>  |
|:-:|:-:|
|**Status**   | ok  |

* withW1+W2+W3+W4+W5 (12635g)

|Angle(°)|<span style="font-weight:normal;color:gray">67</span>  |
|:-:|:-:|
|**Status**   | ok  |

* withW1+W2+W3+W4+W6 (19110g)

|Angle(°)|<span style="font-weight:normal;color:gray">67</span>  |
|:-:|:-:|
|**Status**   | ok  |



#### Polyamide 6 (PA6)

* W1+W2+W3+W4+W6 (19110g)

|Angle(°)|<span style="font-weight:normal;color:gray">67</span>  |
|:-:|:-:|
|**Status**   | ok  |



## Calculation of momentum

* m<span style ="font-size:x-small">L</span> (lever weight) = 1715g
* m<span style ="font-size:x-small">B</span> (backplate weight) = 710g
* l (lever lenght) = 0.7m
* x (distance from center of mass of the backplate and weights to rotation axis) = 0.65m
* h (height from the lowest point of the pendulum)
* v (speed just before collision)

#### Acryl<br>
a) With no weights at 30° (try before break)<br>
h = 0.09m<br>
v = 1.76 m/s

**L =** m<span style ="font-size:x-small">L</span> &times; (l/2) &times; v + m<span style ="font-size:x-small">B</span> &times; x &times; v = **1.87 kgm²/s**

b)With no waights at 40° (try of break)<br>
h = 0.16m<br>
v = 1.77 m/s

**L =** m<span style ="font-size:x-small">L</span> &times; (l/2) &times; v + m<span style ="font-size:x-small">B</span> &times; x &times; v = **1.88 kgm²/s**

#### Polyoxymethylene (POM)
a) Weights: W1,W2,W3,W4 (9025g) at 67° (try of break)<br>
h = 0.42m<br>
v = 2.9 m/s

**L =** m<span style ="font-size:x-small">L</span> &times; (l/2) &times; v + (m<span style ="font-size:x-small">B</span> + W1 + W2 + W3 + W4) &times; x &times; v = **20.09 kgm²/s**

#### Oleamide & Polyamide 6 (PA6)
a) Weights: W1,W2,W3,W4,W6 (19110g) at 60° (try of break)<br>
h = 0.35m<br>
v = 2.6 m/s

**L =** m<span style ="font-size:x-small">L</span> &times; (l/2) &times; v + (m<span style ="font-size:x-small">B</span> + W1 + W2 + W3 + W4 + W6) &times; x &times; v = **33.35 kgm²/s**

## Conclusion
At the beginning we increased the angles and weights very slowly. After the acrylic case broke so quickly we were even more careful because we thought the other cases would break shortly after the acrylic one, but we were surprised. The POM case exceeded our expectations and just wouldn't break. We started increasing the weights more drastically and finally it gave in at an already very high load. After that we tried the same load on the remaining two cases and they both survived the crash. After that we wanted to see how far we can go and put on all the weights we could fit on the backplate to hit the PA6 case and the oleamide case but still none of them would break at a load of almost 20kg.

Looking at the results it's clear that acryl isn't fit for our purpose because it already broke without any weights put on the pendulum. POM was already surprisingly strong and exceeded our expectations. We couldn't break the oleamide and PA6 cases.

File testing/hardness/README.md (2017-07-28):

# Hardness test report

## Goal

Our goal was to see which material absorbs most force at the given shape and to try and simulate a scenario of use of the case. The turtles clean their shells by rubbing them at rocks. Because the turtle is very heavy it would create lots of force if it hits the spot where the case is mounted. We wanted to know if the tested cases can survive a hit such with high force.

## Equipment

We have built a pendulum like construction. There is a 73cm long lever with its axis of rotation on a screw that is mounted on a two part holder mounted on the table. The screw is held by two bearings to help make the rotation smoother. There is a nut on the screw between the lever and the holder to keep some distance. At the other end of the lever there's a backplate mounted with two screws on the lever with two long screws heading out in the opposite direction where you can put on the weights. On the opposite side of the lever there's a small sphere, witch hits the target case. On the ground there is a holder that holds the tested case in place. It's mounted on a heavy wooden block. There is a board that shows angles (10°, 20°, 30°, 50°, 60°, 67°) mounted on the table.





#### Tested materials
*	Acryl (transparent) - weight: 88g
* Polyamide (black) - weight: 102g
* Oleamide (green) - weight: 83g
* PA6 (white) - weight: 83g

## Testing

To see witch material absorbs most force we let the pendolum crash into the case with different weights from different angles.

We pulled the pendulum up to a certain angle and let it crash into the tested case. After the first crash we stopped it to prevent it from crashing again. We tried to keep the number of hits as low as possible so the case wouldn't break because of the number of crashes rather than the force of the hit. We started on low angles and worked our way up. We started our testing without any weights on to get an approximation of what the cases can handle. The Acrylic case broke very fast without any weights on. After that we started putting more and more weights on the backplate of the pendulum and the cases held up more than we expected. The polyamide case finally broke with already very heavy weights on and the oleamide and PA6 cases wouldn't even break with the all the weights on we could fit on the backplate.



#### Weights:
* weight 1 (W1): 1140g
* weight 2 (W2): 825g
* weight 3 (W3): 2075g
* weight 4 (W4): 4985g
* weight 5 (W5): 3610g
* weight 6 (W6): 10085g

#### Equipment weight:
* lever: 1715g
* backplate: 710g

## Results
#### Acryl
* no add. weights

|Angle(°)|<span style="font-weight:normal;color:gray">20</span>  |<span style="font-weight:normal;color:gray">30</span>  |<span style="font-weight:normal;color:gray">40</span>    |
|:-:|:-:|:-:|:-:|
|**Status**   | ok  |ok  |broken|

#### Polyamide
* no add. weights

|Angle(°)|<span style="font-weight:normal;color:gray">67</span>  |
|:-:|:-:|
|**Status**   | ok  |

* with W1 (1140g)

|Angle(°)|<span style="font-weight:normal;color:gray">30</span>  |<span style="font-weight:normal;color:gray">40</span>  |<span style="font-weight:normal;color:gray">50</span> |<span style="font-weight:normal;color:gray">67</span>    |
|:-:|:-:|:-:|:-:|:-:|
|**Status**   | ok  |ok  |ok |ok

* -with W1 + W2 (1965g)

|Angle(°)|<span style="font-weight:normal;color:gray">50</span>  |<span style="font-weight:normal;color:gray">67</span>
|:-:|:-:|:-:|
|**Status**   | ok  |ok

* with W2+W3 (2900g)

|Angle(°)|<span style="font-weight:normal;color:gray">50</span>  |<span style="font-weight:normal;color:gray">67</span>
|:-:|:-:|:-:|
|**Status**   | ok  |ok

* with W1+W2+W3 (4040g)

|Angle(°)|<span style="font-weight:normal;color:gray">67</span>  |
|:-:|:-:|
|**Status**   | ok  |

* with W1+W2+W3+W4 (9025g)

|Angle(°)|<span style="font-weight:normal;color:gray">50</span>  |<span style="font-weight:normal;color:gray">67</span>
|:-:|:-:|:-:|
|**Status**   | ok  |ok



#### Oleamide

* with W1+W2+W3+W5 (7650g)

|Angle(°)|<span style="font-weight:normal;color:gray">67</span>  |
|:-:|:-:|
|**Status**   | ok  |

* with W1+W2+W3+W4 (9025g)

|Angle(°)|<span style="font-weight:normal;color:gray">67</span>  |
|:-:|:-:|
|**Status**   | ok  |

* withW1+W2+W3+W4+W5 (12635g)

|Angle(°)|<span style="font-weight:normal;color:gray">67</span>  |
|:-:|:-:|
|**Status**   | ok  |

* withW1+W2+W3+W4+W6 (19110g)

|Angle(°)|<span style="font-weight:normal;color:gray">67</span>  |
|:-:|:-:|
|**Status**   | ok  |



#### PA6

* W1+W2+W3+W4+W6 (19110g)

|Angle(°)|<span style="font-weight:normal;color:gray">67</span>  |
|:-:|:-:|
|**Status**   | ok  |



## Calculation of momentum

* m<span style ="font-size:x-small">L</span> (lever weight) = 1715g
* m<span style ="font-size:x-small">B</span> (backplate weight) = 710g
* l (lever lenght) = 0.7m
* x (distance from center of mass of the backplate and weights to rotation axis) = 0.65m
* h (height from the lowest point of the pendulum)
* v (speed just before collision)

#### Acryl<br>
a) With no weights at 30° (try before break)<br>
h = 0.09m<br>
v = 1.76 m/s

**L =** m<span style ="font-size:x-small">L</span> &times; (l/2) &times; v + m<span style ="font-size:x-small">B</span> &times; x &times; v = **1.87 kgm²/s**

b)With no waights at 40° (try of break)<br>
h = 0.16m<br>
v = 1.77 m/s

**L =** m<span style ="font-size:x-small">L</span> &times; (l/2) &times; v + m<span style ="font-size:x-small">B</span> &times; x &times; v = **1.87 kgm²/s**

#### Polyamide
a) Weights: W1,W2,W3,W4 (9025g) at 67° (try of break)<br>
h = 0.42m<br>
v = 2.9 m/s

**L =** m<span style ="font-size:x-small">L</span> &times; (l/2) &times; v + (m<span style ="font-size:x-small">B</span> + W1 + W2 + W3 + W4) &times; x &times; v = **1.87 kgm²/s**

#### Oleamide & PA6
a) Weights: W1,W2,W3,W4,W6 (19110g) at 60° (try of break)<br>
h = 0.35m<br>
v = 2.6 m/s

**L =** m<span style ="font-size:x-small">L</span> &times; (l/2) &times; v + (m<span style ="font-size:x-small">B</span> + W1 + W2 + W3 + W4 + W6) &times; x &times; v = **1.87 kgm²/s**

## Summary
At the beginning we increased the angles and weights very slowly. After the acrylic case broke so quickly we were even more careful because we thought the other cases would break shortly after the acrylic one, but we were surprised. The polyamide case exceeded our expectations and just wouldn't break. We started increasing the weights more drastically and finally it gave in at an already very high load. After that we tried the same load on the remaining two cases and they both survived the crash. After that we wanted to see how far we can go and put on all the weights we could fit on the backplate to hit the PA6 case and the oleamide case and both it still wouldn't break at a load of almost 20kg.

Looking at the results it's clear that acryl isn't fit for our purpose because it already broke without any weights put on the pendulum. Polyamide was already surprisingly strong and exceeded our expectations and oleamide and PA6 we couldn't even break.

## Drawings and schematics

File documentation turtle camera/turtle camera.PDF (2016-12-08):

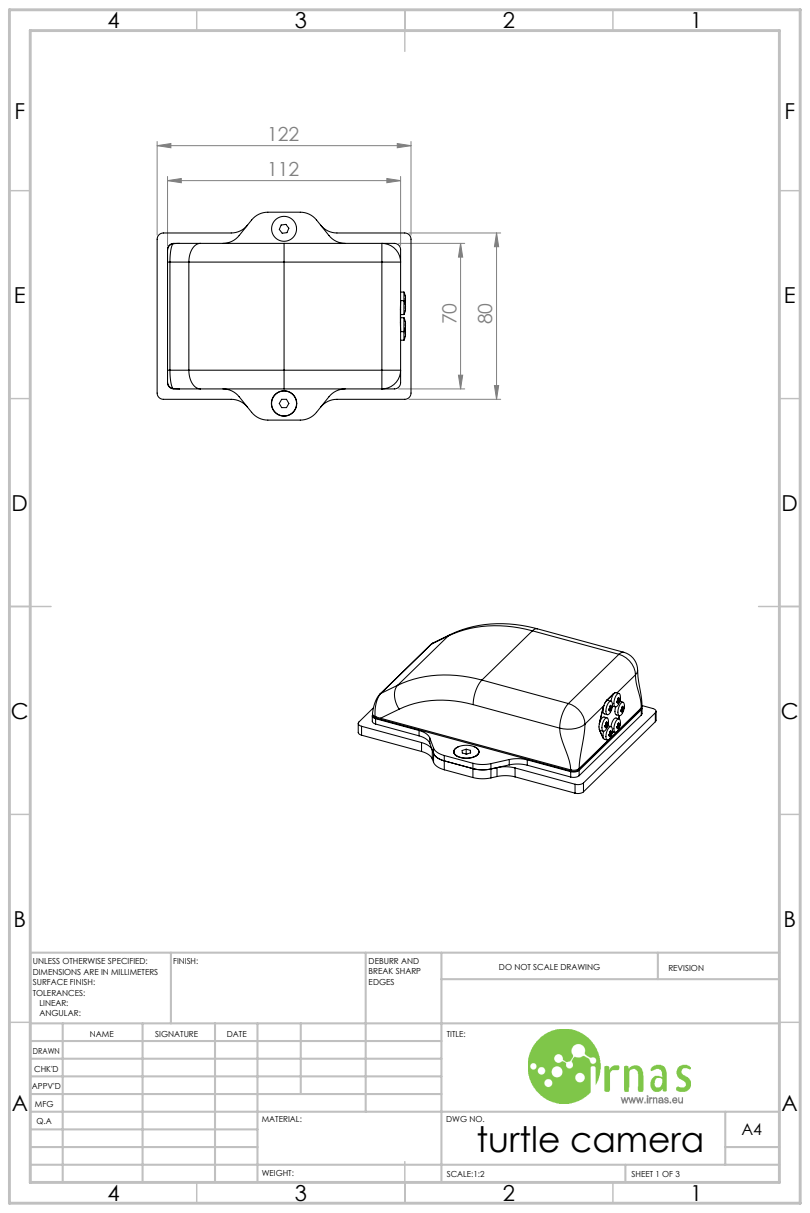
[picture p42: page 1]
FINISH:; DEBURR AND; BREAK SHARP; DO NOT SCALE DRAWING; REVISION; SCALE:1:2; SHEET 1 OF 3

UNLESS OTHERWISE SPECIFIED:
DIMENSIONS ARE IN MILLIMETERS
SURFACE FINISH:
TOLERANCES:
LINEAR:
ANGULAR:

NAME | SIGNATURE | DATE | | | | TITLE:

DRAWN
CHK'D
APPV'D
MFG
Q.A | | | | MATERIAL: | DWG NO. turtle camera | A4

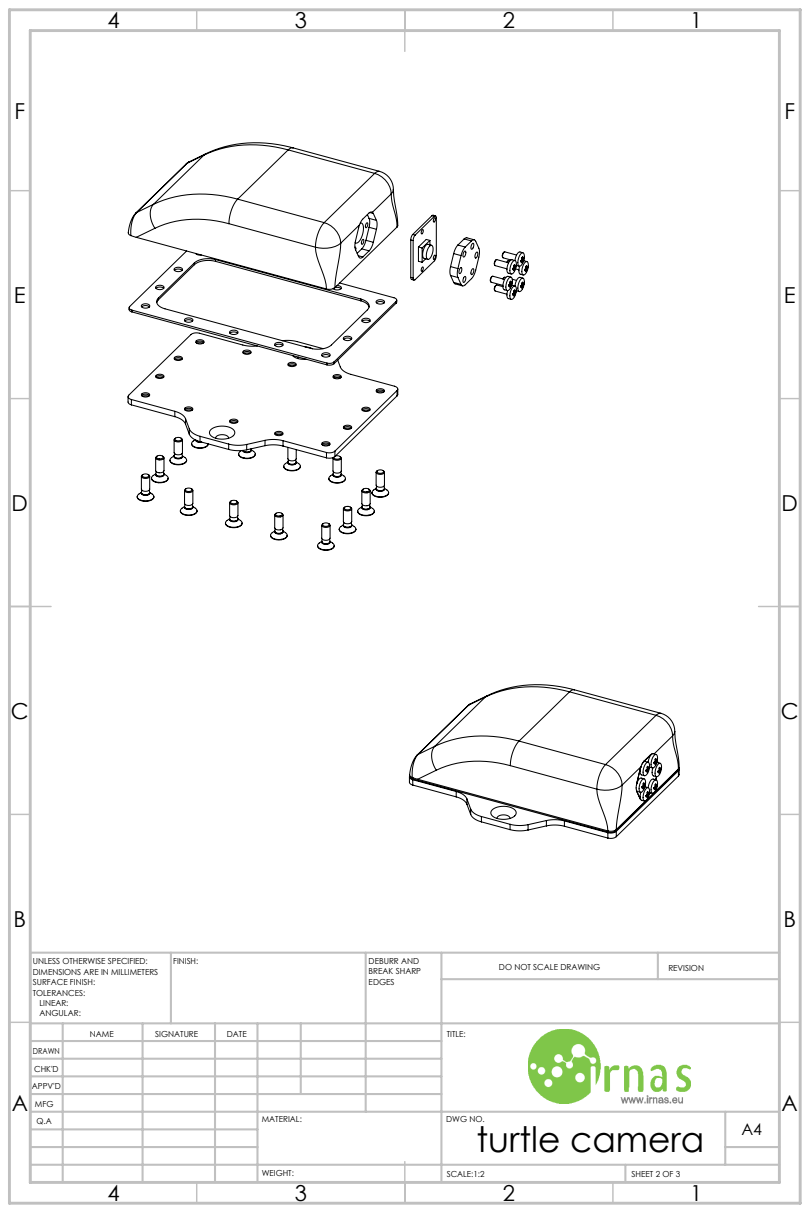
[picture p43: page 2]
FINISH:; DEBURR AND; BREAK SHARP; DO NOT SCALE DRAWING; REVISION

UNLESS OTHERWISE SPECIFIED:
DIMENSIONS ARE IN MILLIMETERS
SURFACE FINISH:
TOLERANCES:
LINEAR:
ANGULAR:

NAME | SIGNATURE | DATE | TITLE:

DRAWN
CHK'D
APPV'D
MFG

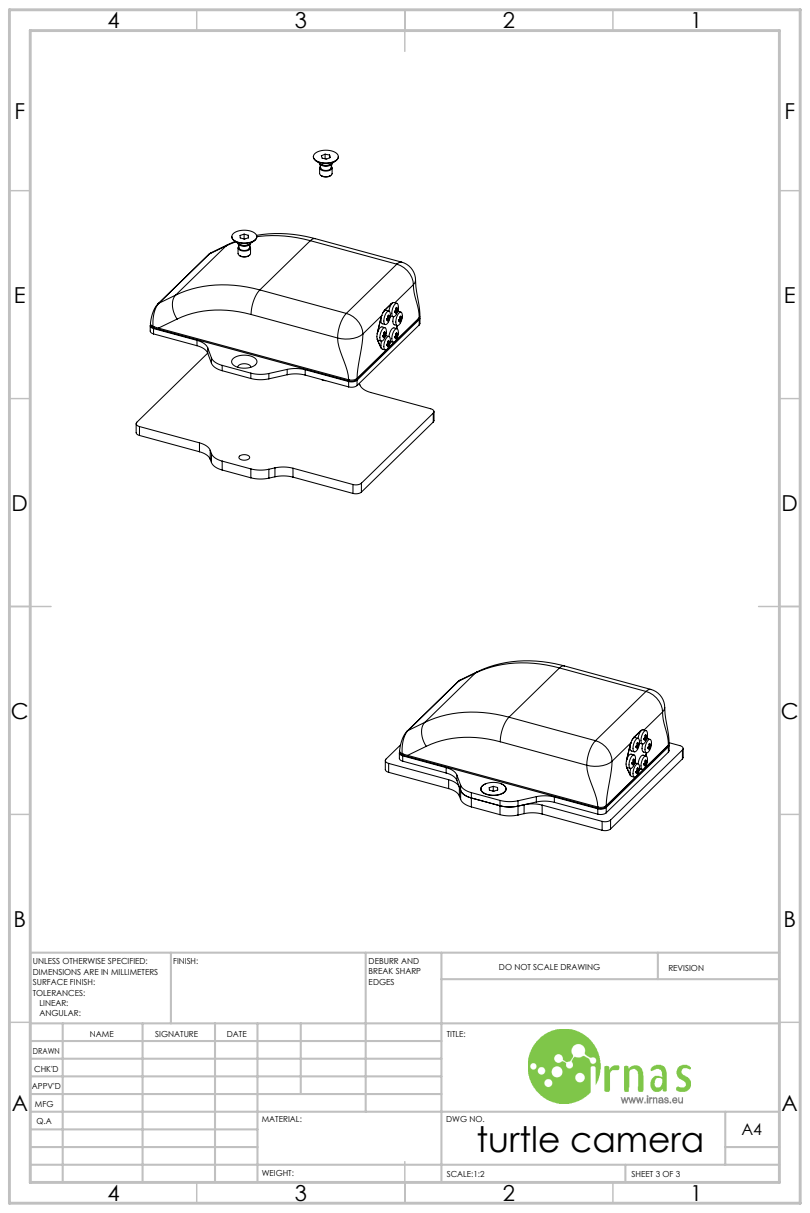
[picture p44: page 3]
FINISH:; DEBURR AND; BREAK SHARP; DO NOT SCALE DRAWING; REVISION

UNLESS OTHERWISE SPECIFIED:
DIMENSIONS ARE IN MILLIMETERS
SURFACE FINISH:
TOLERANCES:
LINEAR:
ANGULAR:

NAME | SIGNATURE | DATE | TITLE:

DRAWN
CHK'D
APPV'D
MFG

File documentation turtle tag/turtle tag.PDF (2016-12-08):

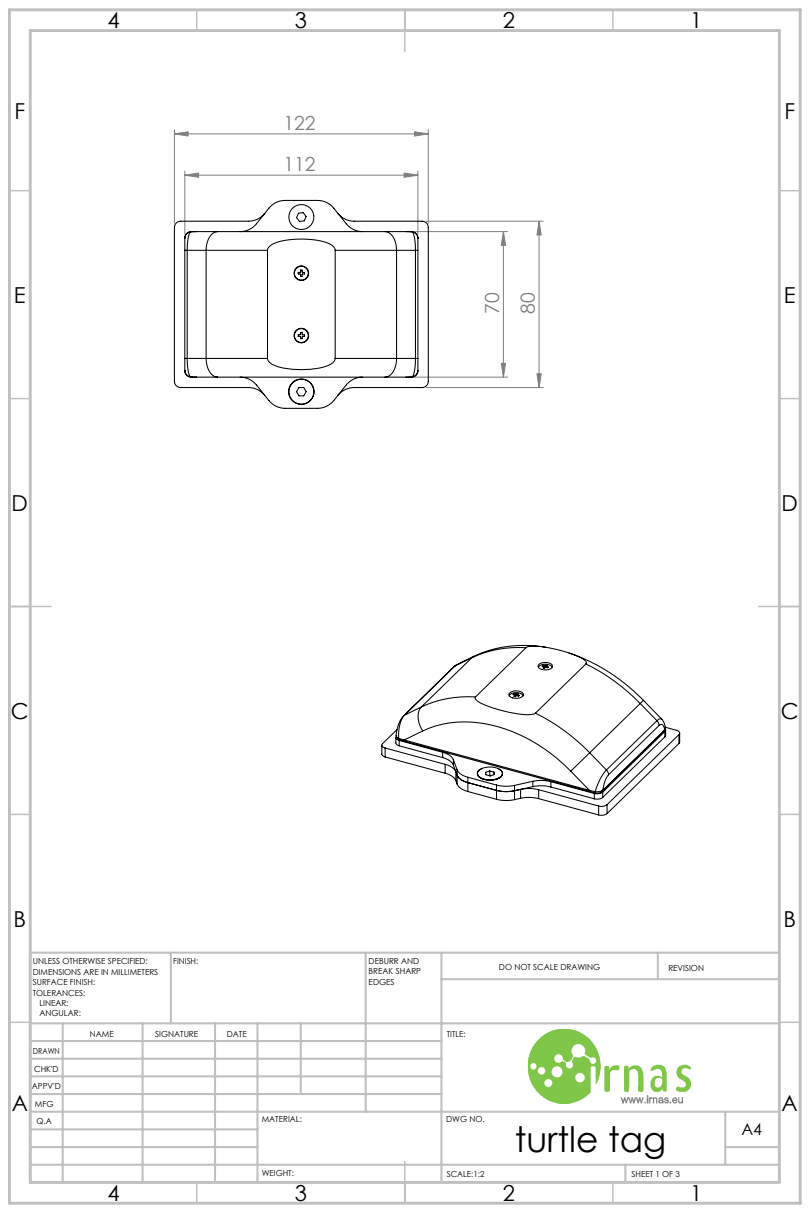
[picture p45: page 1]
FINISH:; DEBURR AND; BREAK SHARP; DO NOT SCALE DRAWING; REVISION; SCALE:1:2; SHEET 1 OF 3

UNLESS OTHERWISE SPECIFIED:
DIMENSIONS ARE IN MILLIMETERS
SURFACE FINISH:
TOLERANCES:
LINEAR:
ANGULAR:

NAME | SIGNATURE | DATE | | | | TITLE:

DRAWN
CHK'D
APPV'D
MFG
Q.A | | | | MATERIAL: | DWG NO. turtle tag | A4

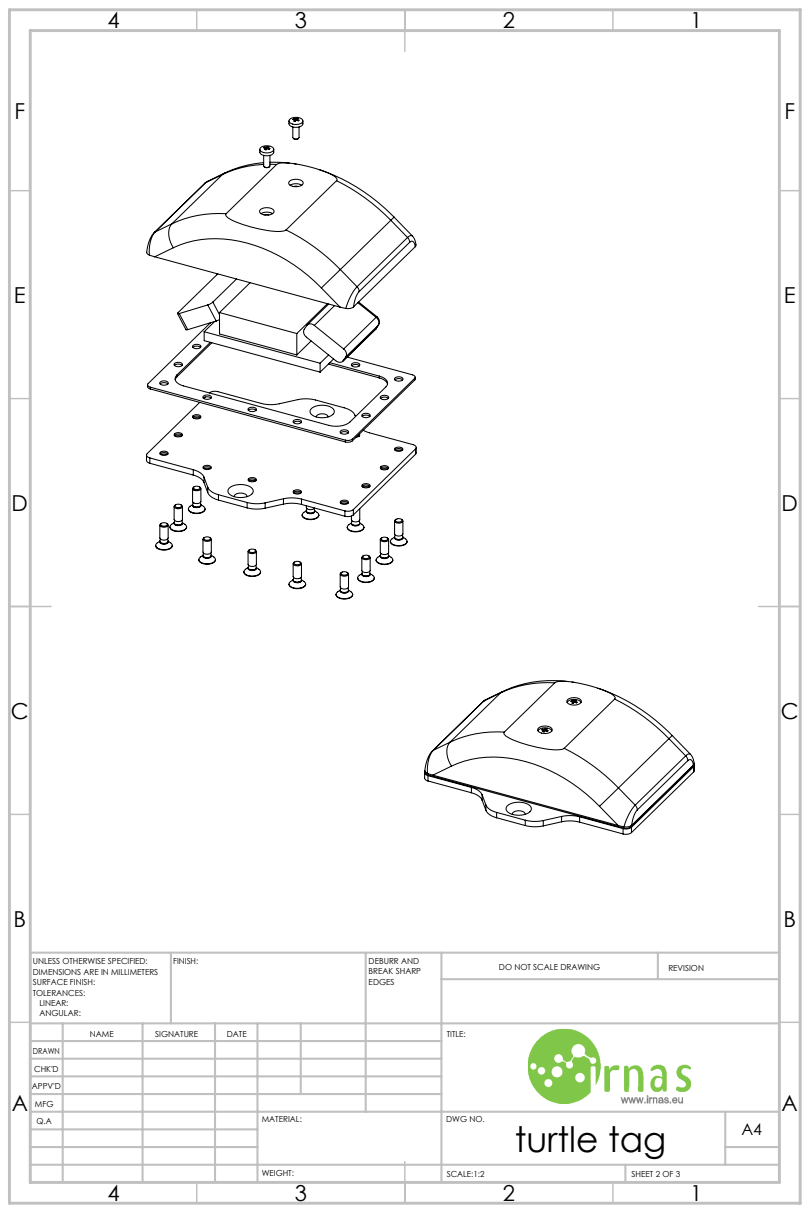
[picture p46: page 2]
FINISH:; DEBURR AND; BREAK SHARP; DO NOT SCALE DRAWING; REVISION

UNLESS OTHERWISE SPECIFIED:
DIMENSIONS ARE IN MILLIMETERS
SURFACE FINISH:
TOLERANCES:
LINEAR:
ANGULAR:

NAME | SIGNATURE | DATE | TITLE:

DRAWN
CHK'D
APPV'D
MFG

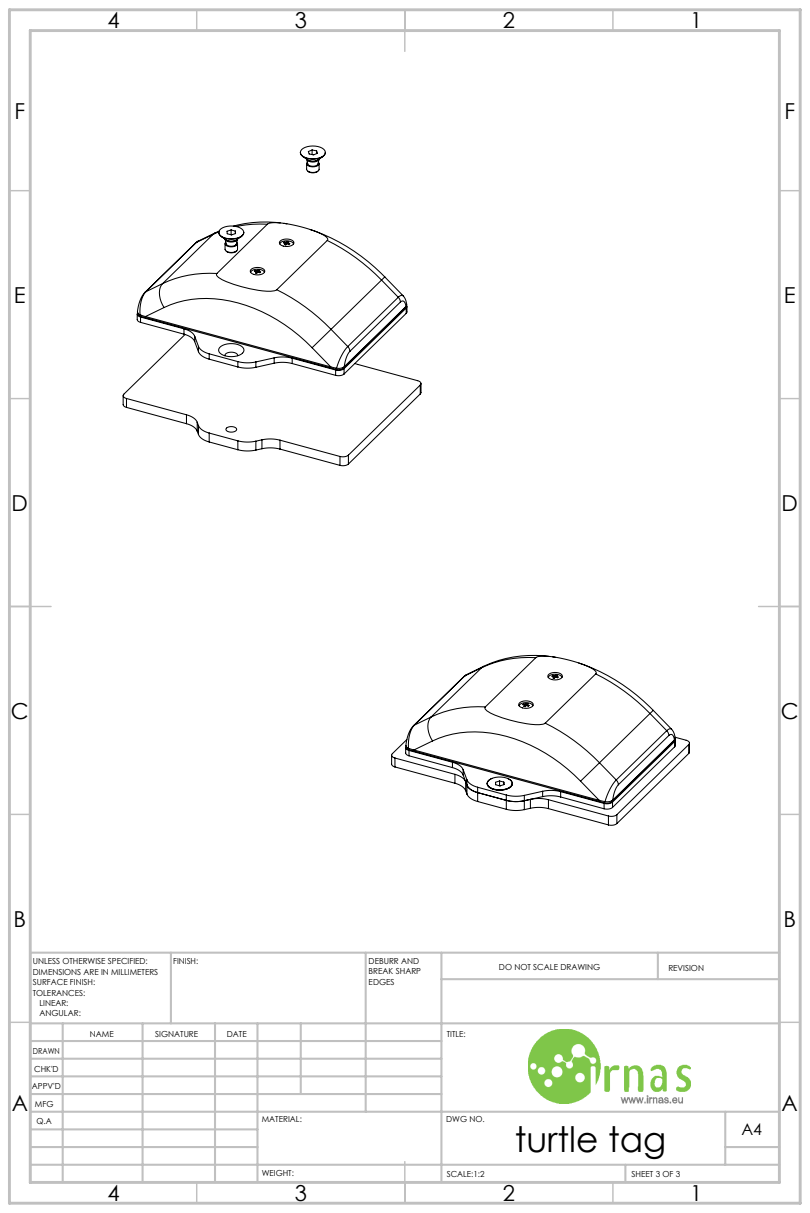
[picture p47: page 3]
FINISH:; DEBURR AND; BREAK SHARP; DO NOT SCALE DRAWING; REVISION

UNLESS OTHERWISE SPECIFIED:
DIMENSIONS ARE IN MILLIMETERS
SURFACE FINISH:
TOLERANCES:
LINEAR:
ANGULAR:

NAME | SIGNATURE | DATE | TITLE:

DRAWN
CHK'D
APPV'D
MFG

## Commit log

2016-01-18 Documentation Upload
    [1050mAh LiPo Bat.SLDPRT, 1050mAh LiPo Bat.STEP, Assem+BOM.DXF, Assem+BOM.SLDDRW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]
2016-12-08 version 2 documentation upload
    [1050mAh LiPo Bat.SLDPRT, 1050mAh LiPo Bat.STEP, AX3.SLDPRT, Assem+BOM.DXF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]
2017-07-27 testing files
    [Assem.SLDASM, DIN 912 M5 x 12.SLDPRT, DIN 912 M8 x 30.SLDPRT, DIN 912 M8 x 60.SLDPRT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]
2017-07-27 changed image names
    [Assembly.SLDASM, DIN 912 M5 x 12.SLDPRT, DIN 912 M8 x 30.SLDPRT, DIN 912 M8 x 60.SLDPRT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]
2017-07-28 updated readme files
    [Assembly.SLDASM, DIN 912 M5 x 12.SLDPRT, DIN 912 M8 x 30.SLDPRT, DIN 912 M8 x 60.SLDPRT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]
2017-11-26 Photos of assembled tag and enclosure
